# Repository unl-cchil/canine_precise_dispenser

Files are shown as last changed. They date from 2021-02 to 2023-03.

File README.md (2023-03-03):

# Raspberry Pi controlled precise treat dispenser
**This project provides the source for a precise canine treat dispenser designed for numerical discrimination tasks.**

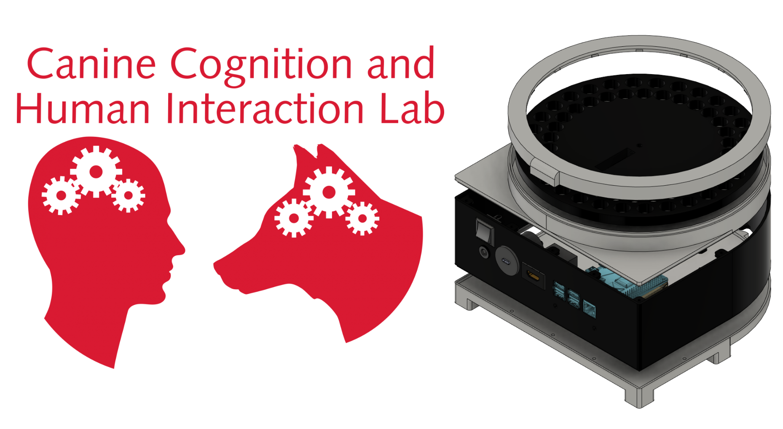
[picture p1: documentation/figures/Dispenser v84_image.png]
Precise Dispenser

### Overview
For detailed overview, review the [user guide](https://github.com/unl-cchil/canine_precise_dispenser/blob/main/documentation/user_guide/unl_cchil_precise_dispenser_guide.pdf) or the [Journal of Open Hardware paper](http://doi.org/10.5334/joh.41).  The basic operating principles of the dispenser can be seen in our [YouTube demo video](https://www.youtube.com/watch?v=fIKlNvzwXUY) or in [this embedded video](https://github.com/unl-cchil/canine_precise_dispenser/blob/main/hardware/dispenser/operation/show_dispenser_video.md).

By using the embedded Python library in the Raspberry Pi image, which is also included in this repository, the stepper motor can be controlled to position the treat holes over the pellet exhaust, leading to a dispensation.  By chaining these events together, a specified quantity of treats can be dispensed.  Additionally, the image is configured with a working build of PsychoPy (v3.2.4).

### Raspberry Pi Image
The SD card image for the Raspberry Pi has all dependencies installed and only needs to have its access point configured using pi-ap.  The image can be found [here](https://drive.google.com/file/d/1Q6JxdohXtvS-_8pmgR74lJ5-K5ArOl2h/view?usp=sharing).  Use an SD card flasher to write this image to a bootable media, such as balenaEtcher, Win32DiskImager, or other similar software.

### Interfacing Example
```
from precise_dispenser_driver import PreciseDispenser

dispenser = PreciseDispenser()
try:
	dispenser.dispense_treats(10)
	print(“Successfully dispensed ten treats.”)
except ValueError as e:
	print(e)
dispenser.close()
```

### License
The hardware is available under a [CERN-OHL-S-2.0 license](https://spdx.org/licenses/CERN-OHL-S-2.0.html), found [here](https://github.com/unl-cchil/canine_precise_dispenser/blob/main/HWLICENSE.md).

The software is available under an [MIT license](https://opensource.org/licenses/MIT), found [here](https://github.com/unl-cchil/canine_precise_dispenser/blob/main/SWLICENSE.md).

The documentation is available under a [Creative Commons Attribution-ShareAlike 4.0 International Public License (CC BY-SA 4.0)](https://creativecommons.org/licenses/by-sa/4.0/), found [here](https://github.com/unl-cchil/canine_precise_dispenser/blob/main/LICENSE.md).

### Project Mentions
[Hackaday](https://hackaday.com/2022/02/06/open-hardware-dog-treat-dispenser-is-a-stepping-stone-for-behavioral-research/), [UNL Pocket Science](https://news.unl.edu/newsrooms/today/article/lab-s-best-friend-3d-printed-dog-treat-dispenser-outperforms-predecessors/)

### Contact
This project was conducted by the [Canine Cognition and Human Interaction Lab](https://dogcog.unl.edu). For questions, please contact the developer Walker Arce (warce@unomaha.edu) or the principal investigator Jeffrey R. Stevens (jeffrey.r.stevens@gmail.com).

### Citation
Arce, W., and Stevens, J. R. (2022). A precise dispenser design for canine cognition research. _Journal of Open Hardware_, 6(1), 2. http://doi.org/10.5334/joh.41

### Funding
This research was supported by a National Science Foundation grant (SES-1658837) and a University of Nebraska-Lincoln Research Council Grant-in-Aid to JRS.

### Dataset Metadata
The following table is necessary for this dataset to be indexed by search
engines such as <a href="https://g.co/datasetsearch">Google Dataset Search</a>.
<div itemscope itemtype="http://schema.org/Dataset">
<table>
<tr>
<th>property</th>
<th>value</th>
</tr>
<tr>
<td>name</td>
<td><code itemprop="name">A precise dispenser design for canine cognition research reliability testing dataset</code></td>
</tr>
<tr>
<td>description</td>
<td><code itemprop="description">The dataset from the paper [A precise dispenser design for canine cognition research](http://doi.org/10.5334/joh.41). We tested five treat dispensers 100 times each with 10 tests of increasing dispensing targets from 1 to 10 treats. Each row of the data file gives the expected and actual number of treats dispensed for a single trial.</code></td>
</tr>
</tr>
<tr>
<td>url</td>
<td><code itemprop="url">https://github.com/unl-cchil/canine_precise_dispenser</code></td>
</tr>
<tr>
<td>sameAs</td>
<td><code itemprop="sameAs">https://github.com/unl-cchil/canine_precise_dispenser</code></td>
</tr>
<tr>
<td>citation</td>
<td><code itemprop="citation">TBA</code></td>
</tr>
<tr>
<td>hw license</td>
<td>
<div itemscope itemtype="http://schema.org/CreativeWork" itemprop="license">
<table>
<tr>
<th>property</th>
<th>value</th>
</tr>
<tr>
<td>name</td>
<td><code itemprop="name">CERN-OHL-S-2.0</code></td>
</tr>
<tr>
<td>url</td>
<td><code itemprop="url">https://spdx.org/licenses/CERN-OHL-S-2.0.html</code></td>
</tr>
</table>
</div>
</td>
</tr>
<tr>
<td>sw license</td>
<td>
<div itemscope itemtype="http://schema.org/CreativeWork" itemprop="license">
<table>
<tr>
<th>property</th>
<th>value</th>
</tr>
<tr>
<td>name</td>
<td><code itemprop="name">MIT</code></td>
</tr>
<tr>
<td>url</td>
<td><code itemprop="url">https://opensource.org/licenses/MIT</code></td>
</tr>
</table>
</div>
</td>
</tr>
<tr>
<td>docs license</td>
<td>
<div itemscope itemtype="http://schema.org/CreativeWork" itemprop="license">
<table>
<tr>
<th>property</th>
<th>value</th>
</tr>
<tr>
<td>name</td>
<td><code itemprop="name">CC BY-SA 4.0</code></td>
</tr>
<tr>
<td>url</td>
<td><code itemprop="url">https://creativecommons.org/licenses/by-sa/4.0/</code></td>
</tr>
</table>
</div>
</td>
</tr>
</table>
</div>

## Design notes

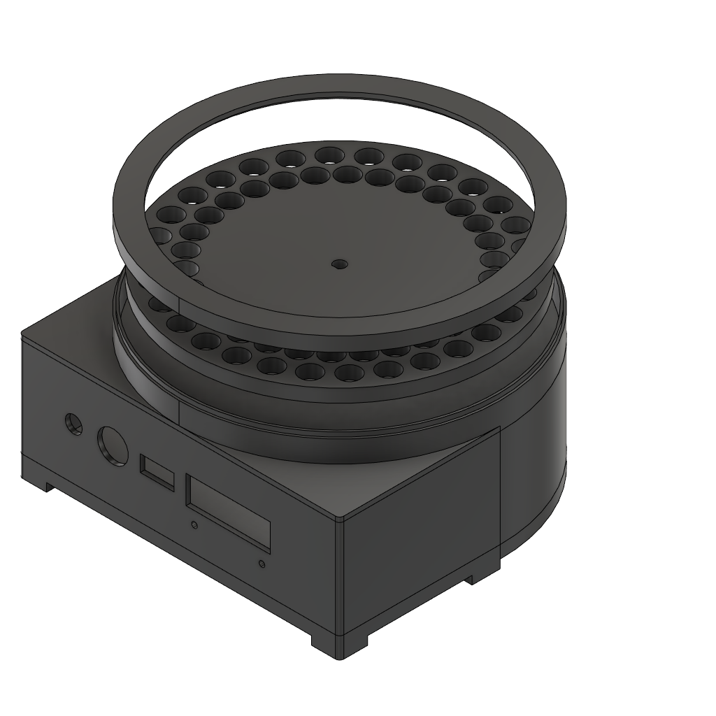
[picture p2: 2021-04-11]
hardware/dispenser/renders/Dispenser v55.png

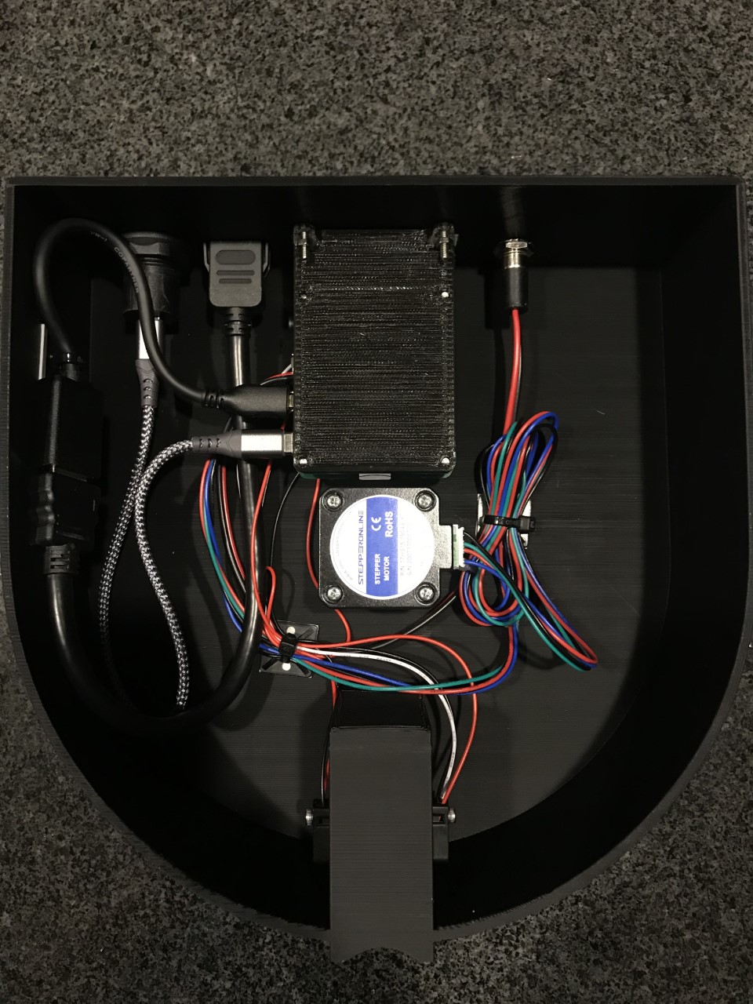
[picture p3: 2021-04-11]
hardware/dispenser/pictures/finished_prototype.jpg

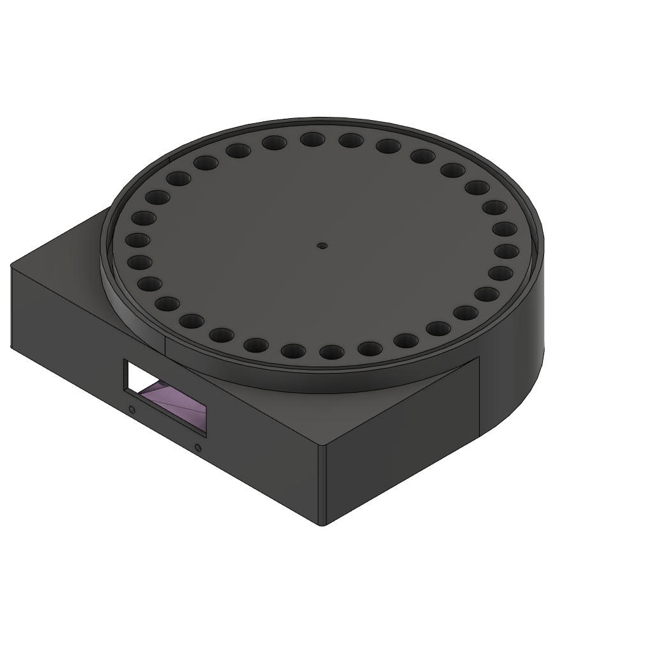
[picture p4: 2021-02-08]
hardware/dispenser/renders/Dispenser v12.png

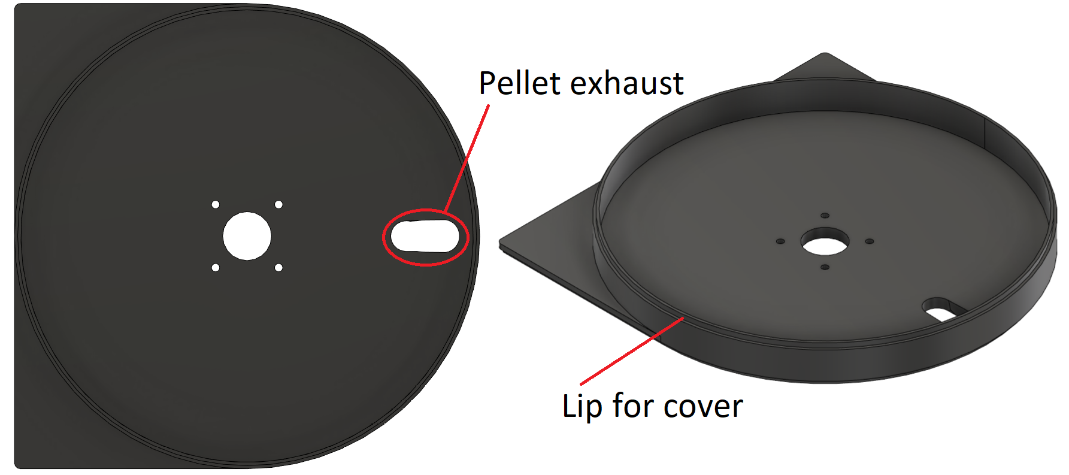
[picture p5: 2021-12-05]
documentation/paper/figures/figure4.png

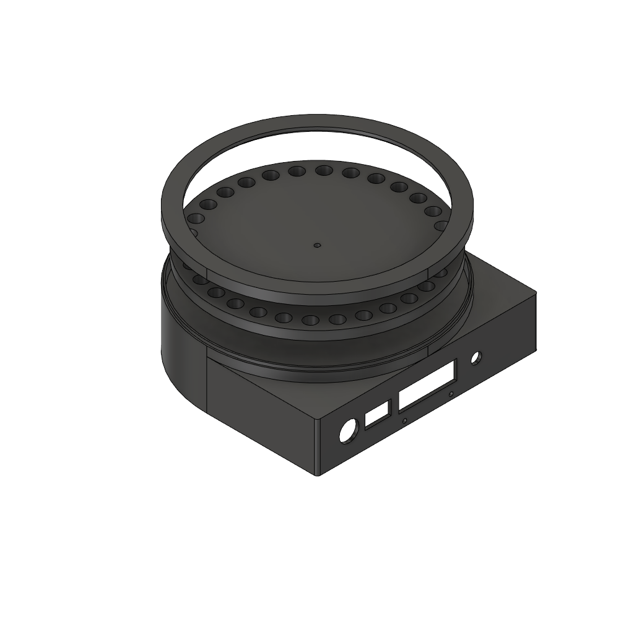
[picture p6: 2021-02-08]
hardware/dispenser/renders/Dispenser v17.png

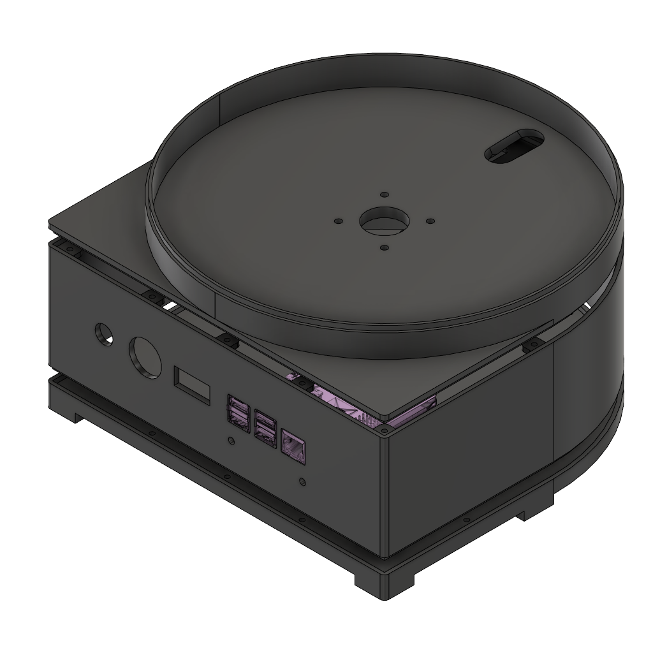
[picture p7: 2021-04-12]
hardware/dispenser/renders/Dispenser v61 - No wheel or cover.png

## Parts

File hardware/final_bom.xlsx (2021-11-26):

Bill of Materials - Precise Dispenser
Part | Quantity | Cost | Link |  | Use
1 kg natural filament | 1 | $22.99 | Filament (https://www.amazon.com/OVERTURE-Filament-Consumables-Dimensional-Accuracy/dp/B07PGY2JP1) | Amazon | Used to print the dispenser
Raspberry Pi 4 | 1 | $75.00 | Raspberry Pi (https://www.sparkfun.com/products/15447) | SparkFun | Controls the dispenser
HDMI Panel Mount | 1 | $7.95 | HDMI (https://www.digikey.com/en/products/detail/4054/1528-2888-ND/9997693?itemSeq=352933947) | DigiKey | Breaks out HDMI connection on Pi to connector panel
USB C Panel Mount | 1 | $7.50 | USB C (https://www.digikey.com/en/products/detail/4261/1528-4261-ND/10287031?itemSeq=352933946) | DigiKey | Breaks out 5V USB power on Pi to connector panel
Barrel Jack Panel Mount | 1 | $5.17 | Barrel Jack (https://www.digikey.com/en/products/detail/10-02879/839-1449-ND/8635386?itemSeq=352933944) | DigiKey | Breaks out 12V power on Pi HAT to connector panel
HDMI to Micro HDMI | 1 | $8.69 | Micro HDMI (https://www.amazon.com/GANA-Adapter-Female-Action-Supported/dp/B07K21HSQX) | Amazon | Converts the HDMI panel connector to Micro HDMI on Pi
Stepper Motor Power Supply | 1 | $11.61 | 12V Power (https://www.digikey.com/en/products/detail/tensility-international-corp/16-00143/10324430) | DigiKey | 12V power supply for stepper motor
Stepper Motor | 1 | $8.99 | Motor (https://www.amazon.com/gp/product/B087BWKJZP/ref=ox_sc_act_title_1?smid=A2TMK1RHV496EY&th=1) | Amazon | Motor to drive the treat jogger
Raspberry Pi Power Supply | 1 | $8.00 | Pi Power (https://www.sparkfun.com/products/15448) | SparkFun | 5V power supply for Raspberry Pi
Plastic Cover | 1 | $11.49 | 8 in Cover (https://www.amazon.com/gp/product/B083HNZWK6/ref=ox_sc_act_title_2?smid=A2PYYAAPQIARBH&psc=1) | Amazon | Acrylic plate to cover the treats from the environment
IR Break Beam | 1 | $6.50 | 5mm IR (https://www.adafruit.com/product/2167) | Adafruit | External sensors to detect a treat falling from jogger
Cable Ties | 1 | $9.69 | Zip Ties and Mounts (https://www.amazon.com/gp/product/B08F77YVYB/ref=ppx_yo_dt_b_asin_title_o00_s00?ie=UTF8&psc=1) | Amazon | Used to hold down wires within the dispenser
Micro SD Card | 1 | $6.49 | SD Card Pack (https://www.amazon.com/Micro-Center-Class-Memory-Adapter/dp/B07K835MNR) | Amazon | Used to hold data and OS on Raspberry Pi
USB C Cable | 1 | $6.99 | USB C Cables (https://www.amazon.com/JXMOX-Charger-Charging-Compatible-2018-Grey/dp/B07TVMBZ75) | Amazon | Connects the panel USB C to Raspberry Pi
Power Switch | 1 | $1.34 | Switch (https://www.digikey.com/en/products/detail/e-switch/RA41G31900/8540802) | DigiKey | Double pull double throw switch for both 5V and 12V power
A4988 Stepper Motor | 1 | $4.69 | Motor Driver (https://www.amazon.com/HiLetgo-Stepstick-Stepper-Printer-Compatible/dp/B00LOF1CA2) | Amazon | Placed on Pi HAT into the female headers
2 Pin Screw Terminal | 2 | $2.20 | 2x 3.5mm Terminal (https://www.digikey.com/en/products/detail/w%C3%BCrth-elektronik/691214110002S/11477397) | DigiKey | Soldered to Pi HAT
3 Pin Screw Terminal | 1 | $1.35 | 3x 3.5mm Terminal (https://www.digikey.com/en/products/detail/w%C3%BCrth-elektronik/691214110003S/11477432) | DigiKey | Soldered to Pi HAT
Capacitor | 1 | $0.13 | 10u TH Cap (https://www.digikey.com/en/products/detail/w%C3%BCrth-elektronik/860240572001/5729254) | DigiKey | Soldered to Pi HAT
Resistor | 1 | $0.10 | 10k TH Res (https://www.digikey.com/en/products/detail/stackpole-electronics-inc/CF14JT10K0/1741265) | DigiKey | Soldered to Pi HAT
40 Pin Header | 1 | $2.29 | Pi Header (https://www.digikey.com/en/products/detail/sullins-connector-solutions/PPTC202LFBN-RC/807240) | DigiKey | Soldered to Pi HAT
Stepper Motor Header | 1 | $0.20 | 4 Pin Right Angle (https://www.digikey.com/en/products/detail/harwin-inc/M20-9750446/3727931) | DigiKey | Soldered to Pi HAT
A4988 Female Pins | 1 | $0.65 | 2x Female Headers (https://www.digikey.com/en/products/detail/sullins-connector-solutions/PPTC081LFBN-RC/810147) | DigiKey | Soldered to Pi HAT

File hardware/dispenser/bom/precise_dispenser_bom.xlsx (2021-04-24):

Bill of Materials - Precise Dispenser
Part | Quantity | Cost | Link
1 kg black filament | 1 | $19.99 | Filament (https://www.amazon.com/OVERTURE-Filament-Consumables-Dimensional-Accuracy/dp/B07PGY2JP1)
Raspberry Pi 4 | 1 | $55.00 | Raspberry Pi (https://www.sparkfun.com/products/15447)
HDMI Panel Mount | 1 | $7.95 | HDMI (https://www.digikey.com/en/products/detail/4054/1528-2888-ND/9997693?itemSeq=352933947)
USB C Panel Mount | 1 | $7.50 | USB C (https://www.digikey.com/en/products/detail/4261/1528-4261-ND/10287031?itemSeq=352933946)
Barrel Jack Panel Mount | 1 | $5.17 | Barrel Jack (https://www.digikey.com/en/products/detail/10-02879/839-1449-ND/8635386?itemSeq=352933944)
HDMI to Micro HDMI | 1 | $8.69 | Micro HDMI (https://www.amazon.com/GANA-Adapter-Female-Action-Supported/dp/B07K21HSQX)
Stepper Motor Power Supply | 1 | $11.61 | 12V Power (https://www.digikey.com/en/products/detail/tensility-international-corp/16-00143/10324430)
Stepper Motor | 1 | $8.99 | Motor (https://www.amazon.com/gp/product/B087BWKJZP/ref=ox_sc_act_title_1?smid=A2TMK1RHV496EY&th=1)
Raspberry Pi Power Supply | 1 | $8.00 | Pi Power (https://www.sparkfun.com/products/15448)
Plastic Cover | 1 | $9.95 | 8 in Cover (https://www.amazon.com/gp/product/B083HNZWK6/ref=ox_sc_act_title_2?smid=A2PYYAAPQIARBH&psc=1)
IR Break Beam | 1 | $1.95 | 3mm IR (https://www.adafruit.com/product/2167)
Cable Ties | 1 | $9.69 | Zip Ties and Mounts (https://www.amazon.com/gp/product/B08F77YVYB/ref=ppx_yo_dt_b_asin_title_o00_s00?ie=UTF8&psc=1)
Micro SD Card | 1 | $6.49 | SD Card Pack (https://www.amazon.com/Micro-Center-Class-Memory-Adapter/dp/B07K835MNR)
USB C Cable | 1 | $6.99 | USB C Cables (https://www.amazon.com/JXMOX-Charger-Charging-Compatible-2018-Grey/dp/B07TVMBZ75)

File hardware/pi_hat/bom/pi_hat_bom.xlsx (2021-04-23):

Bill of Materials - Precise Dispenser Pi HAT
Part | Quantity | Cost | Link
A4988 Stepper Motor | 1 | $4.69 | Motor Driver (https://www.amazon.com/HiLetgo-Stepstick-Stepper-Printer-Compatible/dp/B00LOF1CA2)
2 Pin Screw Terminal | 2 | $2.20 | 2x 3.5mm Terminal (https://www.digikey.com/en/products/detail/w%C3%BCrth-elektronik/691214110002S/11477397)
3 Pin Screw Terminal | 1 | $1.35 | 3x 3.5mm Terminal (https://www.digikey.com/en/products/detail/w%C3%BCrth-elektronik/691214110003S/11477432)
Capacitor | 1 | $0.13 | 10u TH Cap (https://www.digikey.com/en/products/detail/w%C3%BCrth-elektronik/860240572001/5729254)
Resistor | 1 | $0.10 | 10k TH Res (https://www.digikey.com/en/products/detail/stackpole-electronics-inc/CF14JT10K0/1741265)
40 Pin Header | 1 | $2.29 | Pi Header (https://www.digikey.com/en/products/detail/sullins-connector-solutions/PPTC202LFBN-RC/807240)
Stepper Motor Header | 1 | $0.20 | 4 Pin Right Angle (https://www.digikey.com/en/products/detail/harwin-inc/M20-9750446/3727931)
A4988 Female Pins | 2 | $1.30 | 2x Female Headers (https://www.digikey.com/en/products/detail/sullins-connector-solutions/PPTC081LFBN-RC/810147)

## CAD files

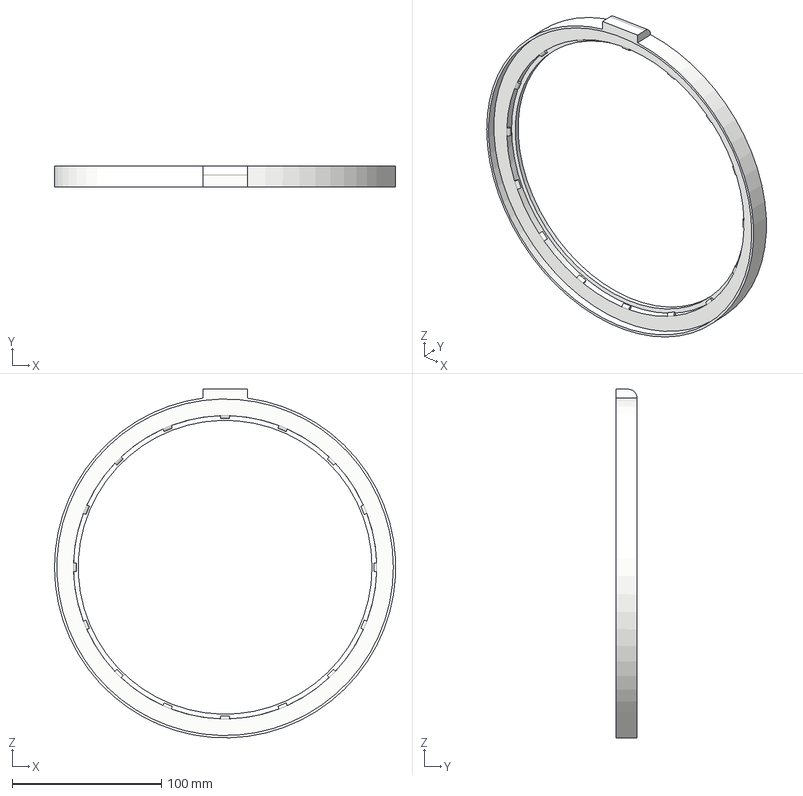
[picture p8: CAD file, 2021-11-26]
hardware/dispenser/step/dispenser_cover.step
228.4 x 14.2 x 233.6 mm

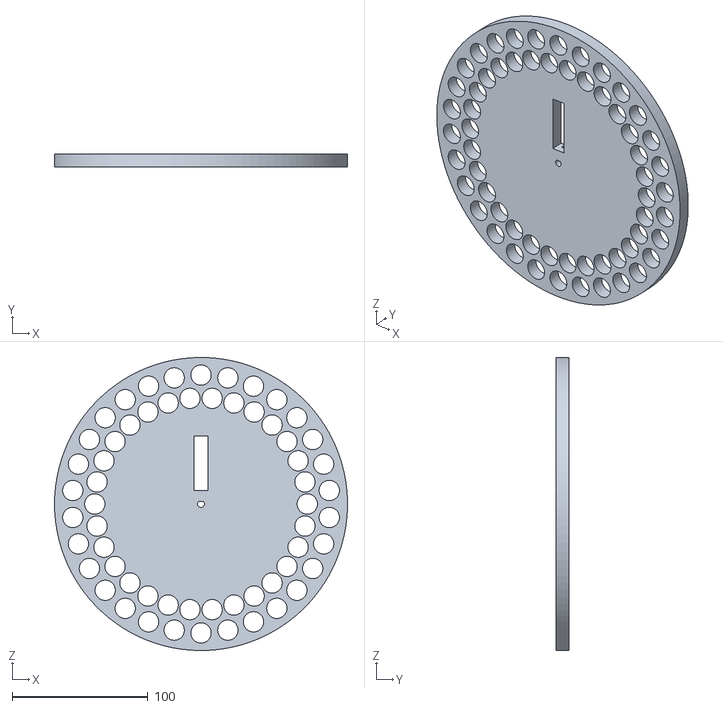
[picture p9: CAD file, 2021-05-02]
hardware/dispenser/stls/dispenser_wheel.stl
215.9 x 9.35 x 215.9

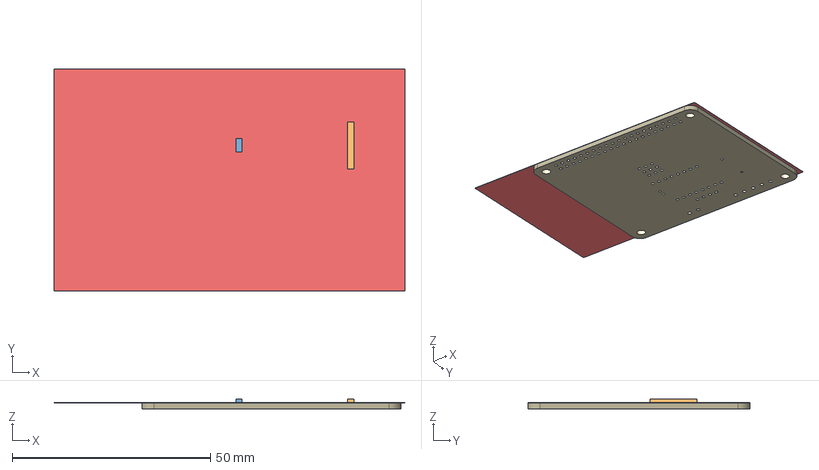
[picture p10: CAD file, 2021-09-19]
hardware/pi_hat/renders/DispenserV2.0.step
88.5 x 56.1 x 2.57 mm
Board
E2-5
SCREWTERMINAL-3.5MM-2 x 2
455-1750-1-ND x 3
A4988
1X04
0207/10
SCREWTERMINAL-3.5MM-3
RASPBERRY_PI_3_MODEL_B+

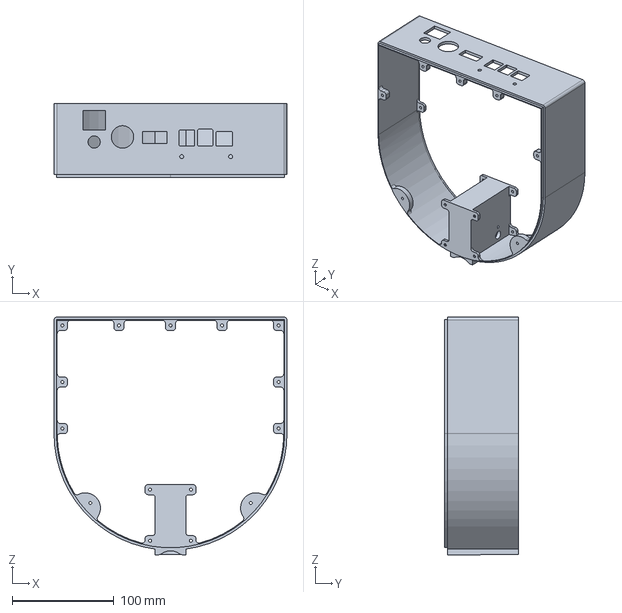
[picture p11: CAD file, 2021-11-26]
hardware/dispenser/step/dispenser_walls.step
228.6 x 72.9 x 233.3 mm

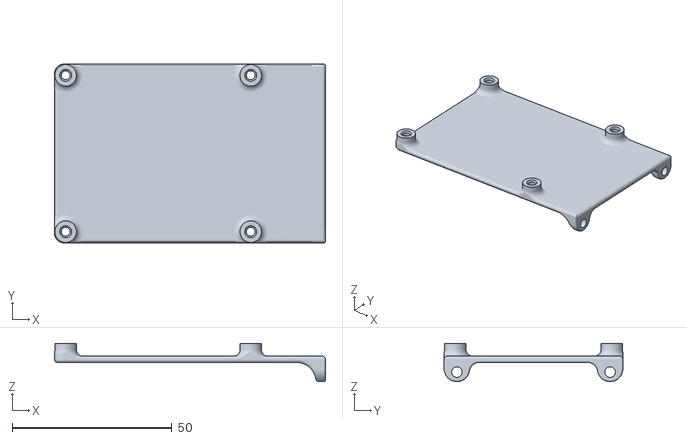
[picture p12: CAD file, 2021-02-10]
hardware/dispenser/stls/dispenser_pi_mount.stl
84.9 x 56.0 x 12.0

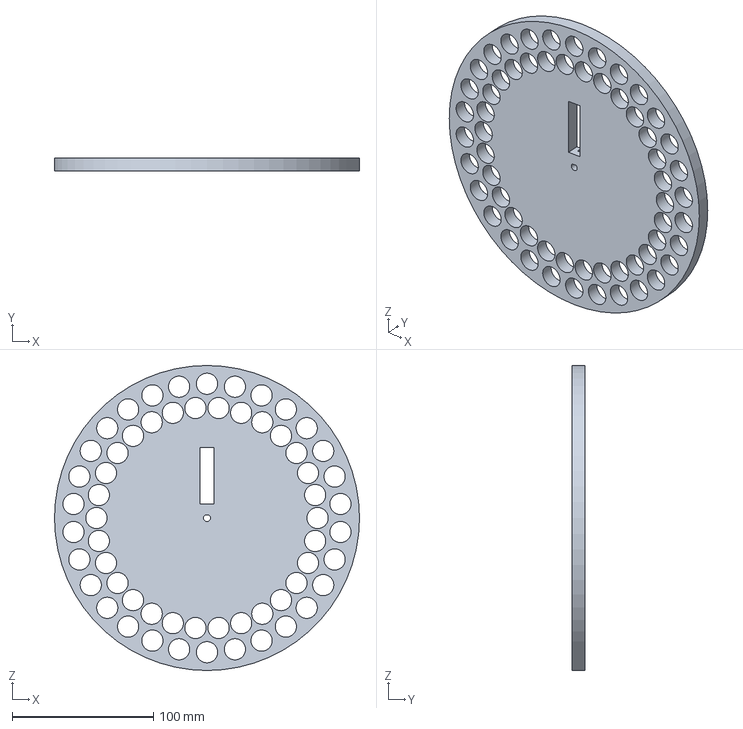
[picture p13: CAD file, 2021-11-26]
hardware/dispenser/step/treat_jogger.step
215.9 x 9.35 x 215.9 mm

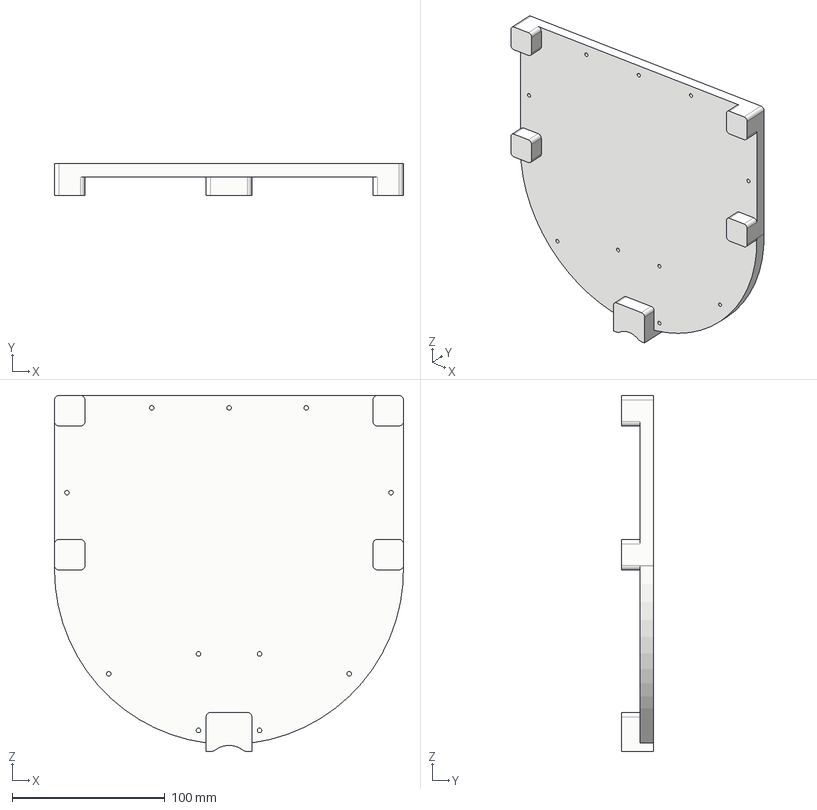
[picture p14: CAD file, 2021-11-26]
hardware/dispenser/step/dispenser_bottom.step
228.6 x 21.0 x 233.3 mm

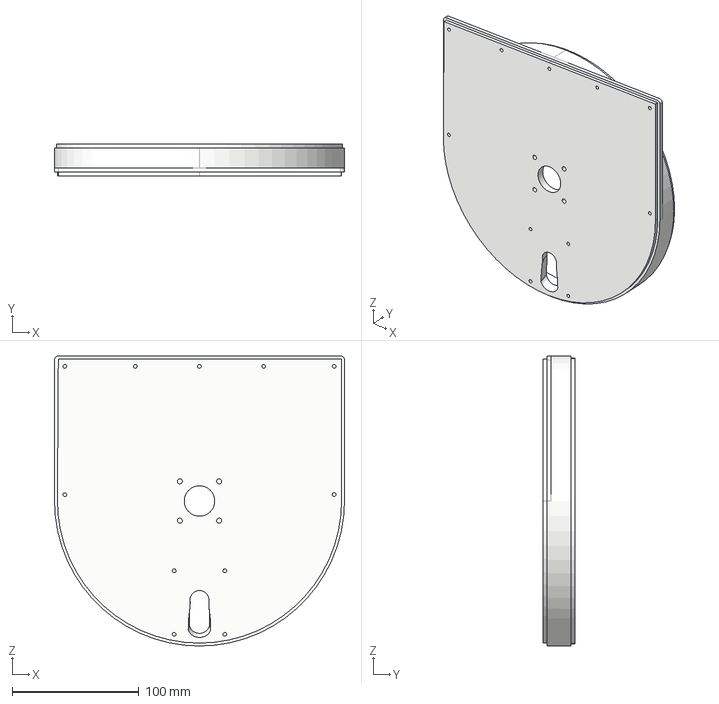
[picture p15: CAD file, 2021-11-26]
hardware/dispenser/step/dispenser_top.step
228.6 x 25.1 x 228.6 mm

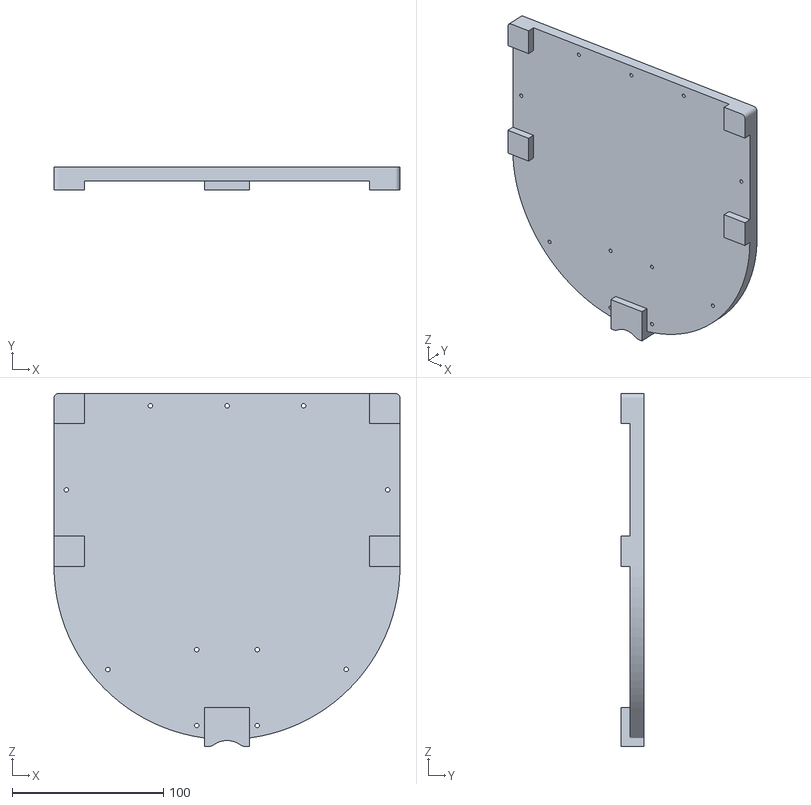
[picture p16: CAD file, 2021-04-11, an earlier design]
hardware/dispenser/stls/Old/dispenser_bottom.stl
228.6 x 15.0 x 233.3

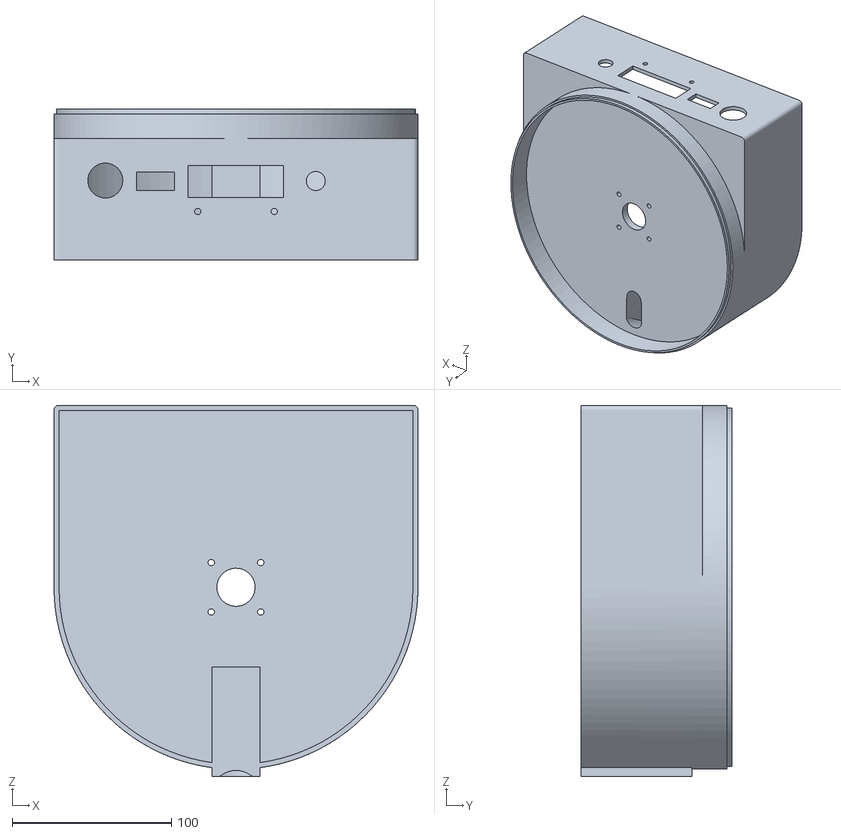
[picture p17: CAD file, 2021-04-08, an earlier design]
hardware/dispenser/stls/Old/dispenser_body.stl
228.6 x 94.9 x 233.3

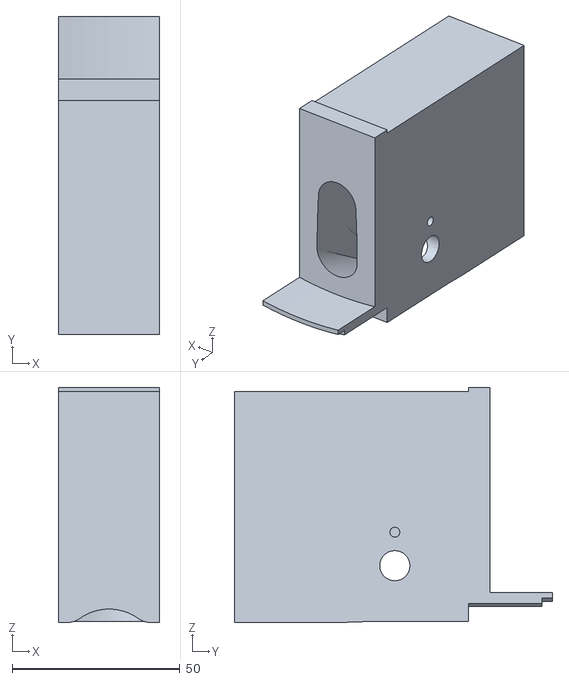
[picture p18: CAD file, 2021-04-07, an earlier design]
hardware/dispenser/stls/Old/dispenser_pellet_exhaust.stl
30.0 x 94.9 x 70.1

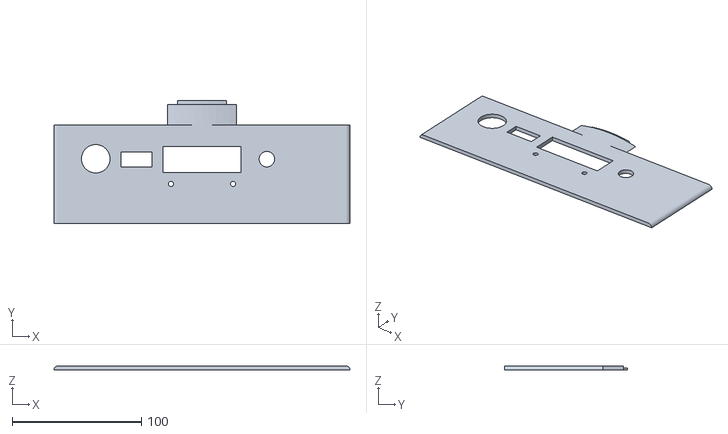
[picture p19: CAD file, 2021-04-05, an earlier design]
hardware/dispenser/stls/Old/dispenser_interface.stl
228.6 x 94.9 x 3.18

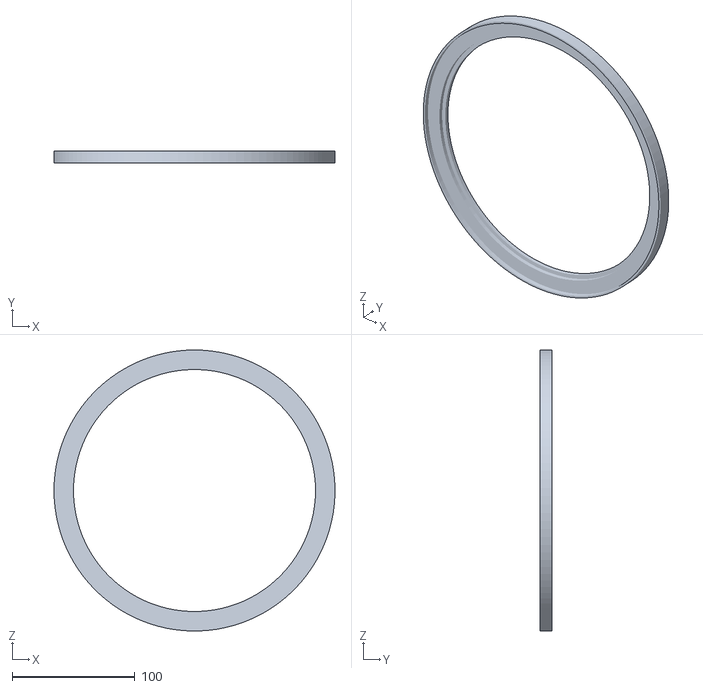
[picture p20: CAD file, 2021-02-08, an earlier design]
hardware/dispenser/stls/Old/dispenser_cover.stl
228.6 x 10.2 x 228.6

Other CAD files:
hardware/dispenser/step/pi_mount.step
hardware/dispenser/stls/Old/dispenser_top.stl
hardware/dispenser/stls/Old/dispenser_walls.stl
hardware/dispenser/stls/Old/dispenser_wheel.stl
hardware/dispenser/source/Dispenser v18.f3d
hardware/dispenser/source/Dispenser v22.f3d
hardware/dispenser/source/Dispenser v30.f3d
hardware/dispenser/source/Dispenser v31.f3d
hardware/dispenser/source/Dispenser v35.f3d
hardware/dispenser/source/Dispenser v39.f3d
hardware/dispenser/source/Dispenser v55.f3d
hardware/dispenser/stls/dispenser_bottom.stl
hardware/dispenser/stls/dispenser_cover.stl
hardware/dispenser/stls/dispenser_top.stl
hardware/dispenser/stls/dispenser_walls.stl

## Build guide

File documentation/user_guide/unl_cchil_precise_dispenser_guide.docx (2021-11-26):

University of Nebraska – Lincoln

Department of Psychology

Canine Cognition and Human Interaction Laboratory

Dr. Jeffrey R. Stevens

Precise Dispenser for Canine Numerical Discrimination Tasks

20 September 2021

V0.4

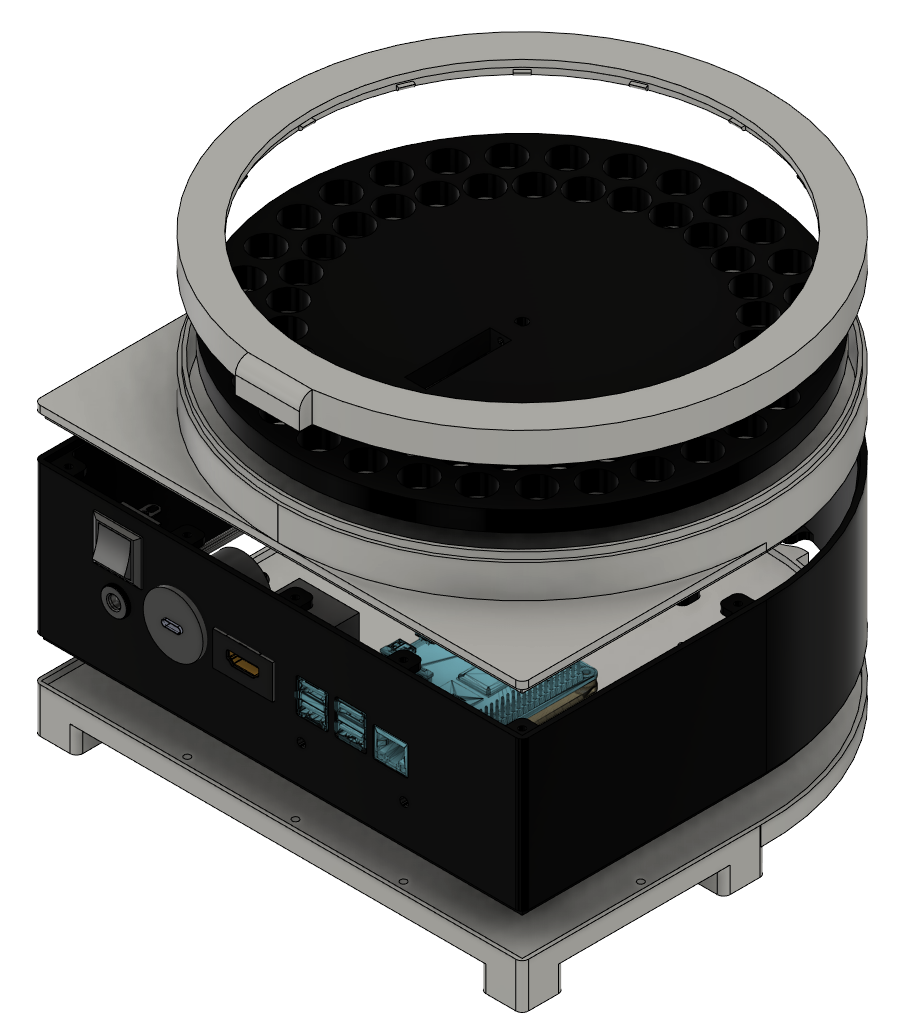
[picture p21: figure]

Figure 1 – Dispenser v84 Render

Overview

The performance of canine numerical discrimination tasks can be hindered by a lack of appropriate instrumentation. Using manual, researcher-controlled instrumentation can introduce a reaction time variable that could impose undue variability in the task results. Therefore, the creation of devices that can automatically dispense precise numbers of treats at the introduction of a predefined stimulus can be justified.

Dispenser Operation

The precise dispenser has a wheel on the top of it that holds up to 59 treats. The stepper motor shaft interfaces to the dispenser wheel through the center hole and by actuating the motor, the holes for the treat lines up with the treat exhaust and falls to the bowl below. When the treat goes through the exhaust it breaks an infrared break beam and the Raspberry Pi detects the treat dispensing.

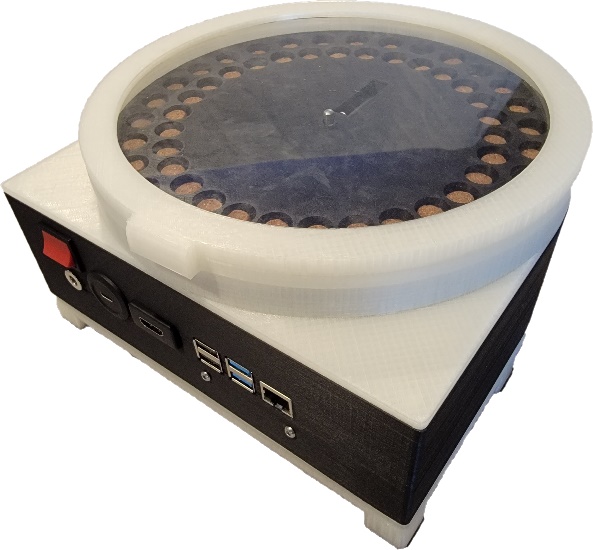
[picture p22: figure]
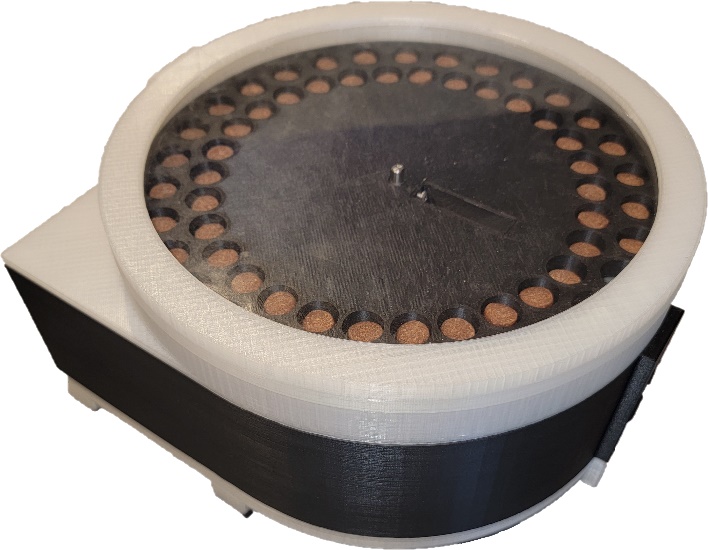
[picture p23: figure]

Figure 2 – Images of the assembled dispenser, fully loaded with treats

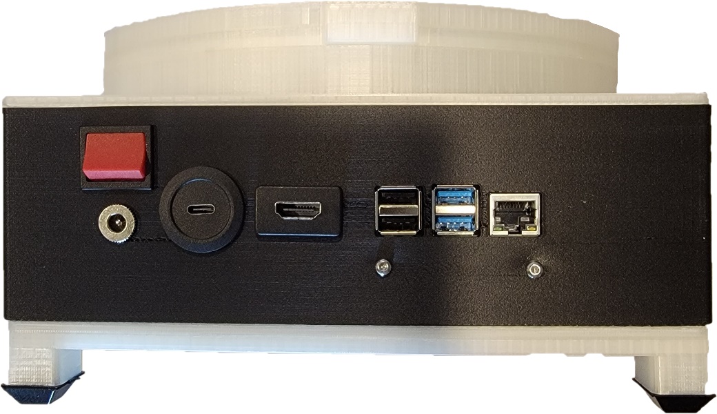
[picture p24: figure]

Figure 3 – Assembled dispenser connector backplane

Build Instructions

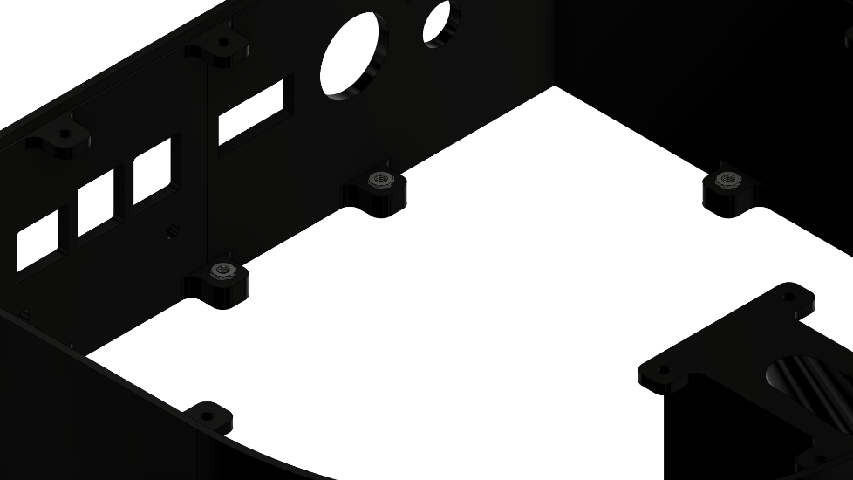
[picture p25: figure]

Observe the M3 hex nut capture slots on the dispenser walls. In each of these, super glue an M3 hex nut. Let it sit for 24 hours before continuing.

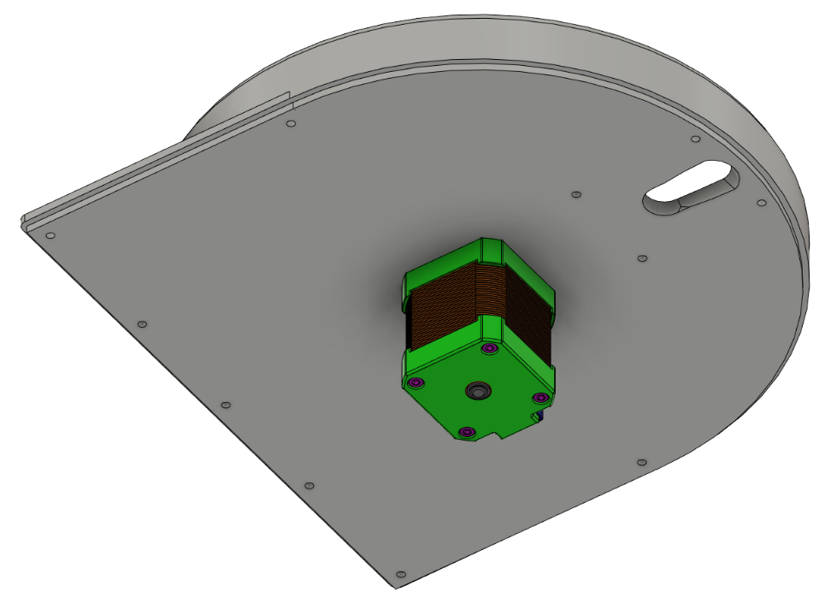
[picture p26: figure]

Mount the Nema 17 stepper motor using pan head M3 screws. Ensure the connector is point towards the right side, as shown.

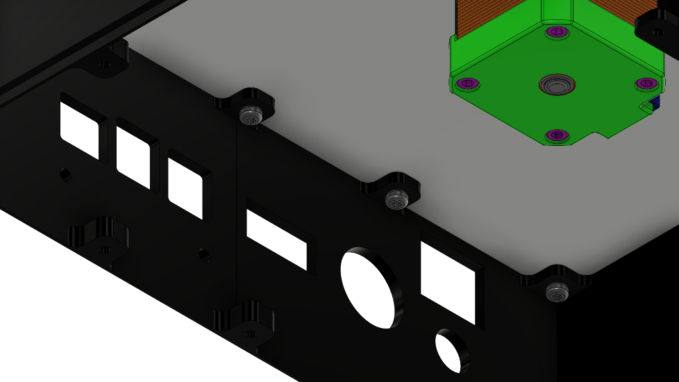
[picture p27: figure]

At this point, use 6mm M3 screws to mount the walls to the top of the dispenser. Mount the dispenser jogger by press fitting it onto the stepper motor shaft. Ensure the motor is supported during this, as it will break through the print when pressing the jogger down.

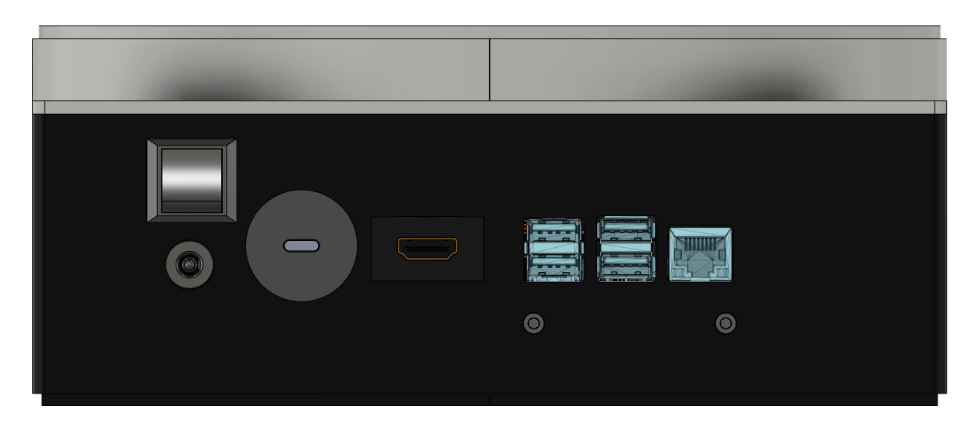
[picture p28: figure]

Now, mount the Raspberry Pi to the right angle mount using four M3 screws. Then, mount this into the walls using a 10mm M3 screw with hex nuts. Then mount the other panel mount connectors into the walls.

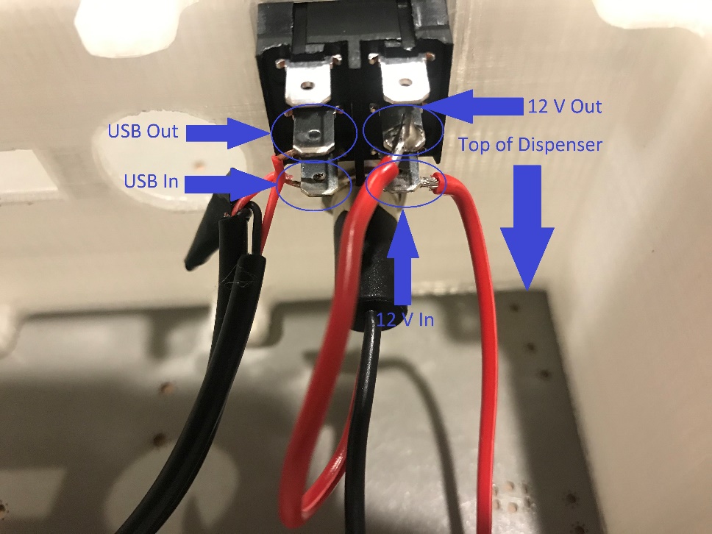
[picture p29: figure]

With the DPDT switch mounted, cut a USB C to USB C cord and solder the grounds back together. Cut the barrel jack panel mount connector’s red wire, with one fifth of it being close to the connector and the other four fifths being used to connect to the Pi HAT. Solder according to image.

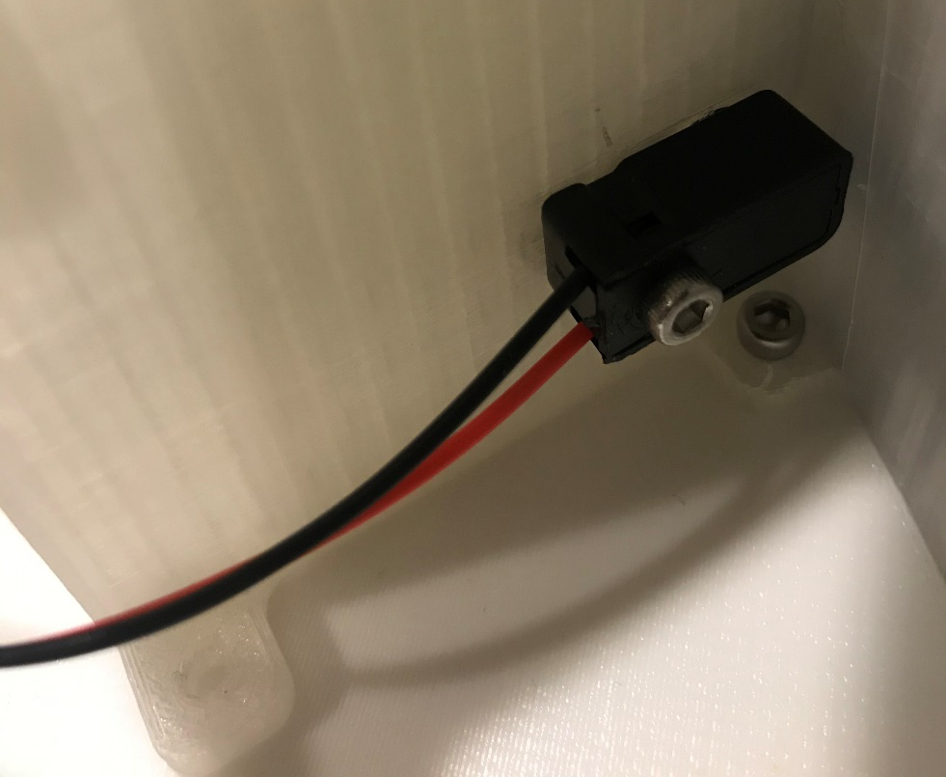
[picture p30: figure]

Mount the IR phototransistor elements to the side of the pellet exhaust using 9mm M3 screws.

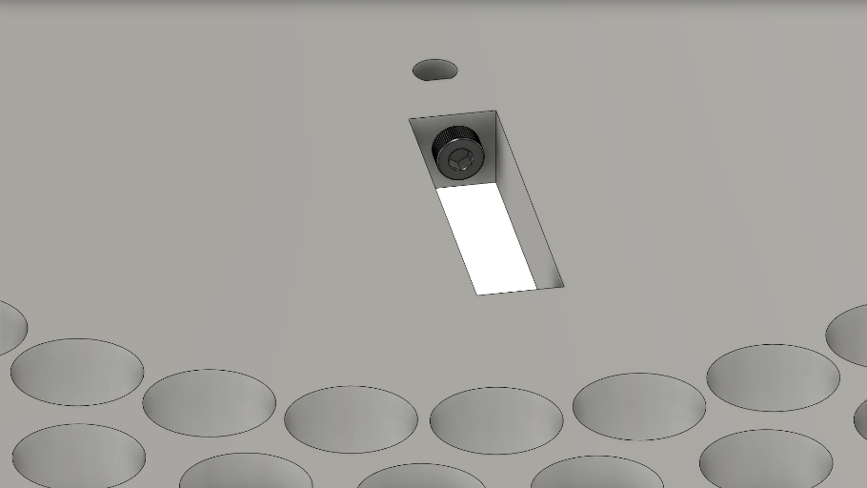
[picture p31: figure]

Place a 12mm M3 in the set screw hole of the treat jogger and screw it down to hold the jogger to the motor shaft.

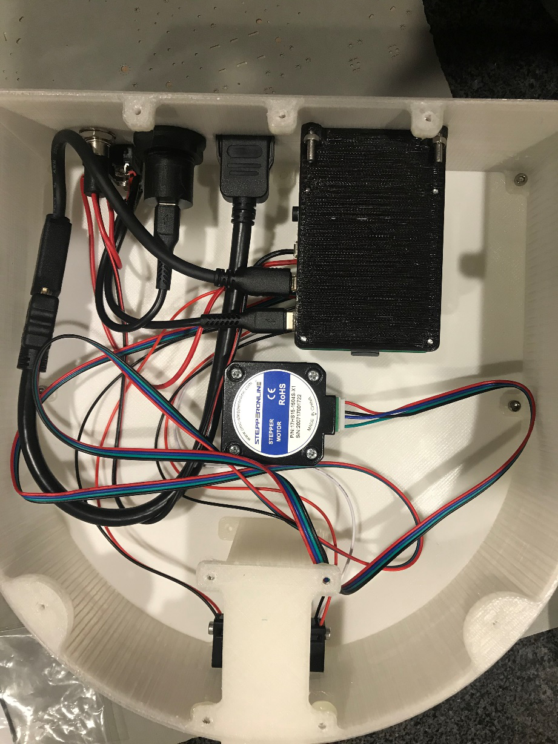
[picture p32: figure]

Wire up the remaining pieces as shown below. Secure the wires using the square zip tie mounts.

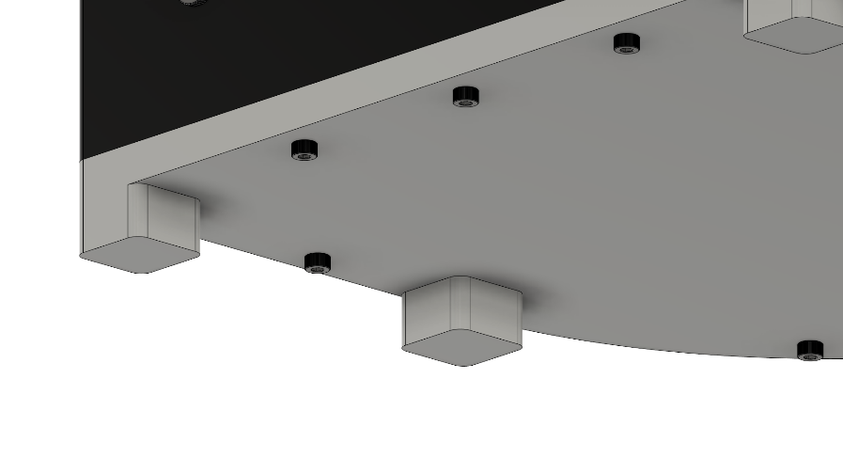
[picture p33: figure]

Screw on the bottom plate using 6mm M3 screws. It is recommended to use rubber anti slip pads on the legs of the dispenser. Place the acrylic disk into the cover and place the cover onto the dispenser.

Testing Operation

1. Place treats into all the holes of the treat jogger and manually rotate the wheel to ensure all treats fall out of the holes. If some stick, then make sure any strands are removed from the print.
2. The dispenser_test.py script can be used to ensure the break beam works and that treats are dispensed as expected.

Troubleshooting

1. If the dispenser under dispenses, ensure the treat jogger is mounted securely to the motor shaft. If the set screw strips the hole, use super glue to affix the wheel to the shaft.
2. If the dispenser over dispenses, ensure that the jogger is perfectly aligned over the pellet exhaust before use.

Python Class Definition

class PreciseDispenser

self.loaded_treats

The number of treats remaining the in the jogger

self.dispensing_timeout

The amount of time between IR break beam events before an exception is thrown

self.dispensing

A Boolean to track if the dispenser is currently dispensing

__init__(loaded_treats, timeout=1)

Initializer for the canine treat dispenser, configures control variables and Pi GPIO.

:param loaded_treats: The number of treats that are loaded into the dispenser for this session. Defaults to max, 59 treats.

:param timeout: The amount of time before the dispenser throw an error between dispensation events

dispense_treat()

Function to dispense a single treat. Should not be used, use dispense_treats for error handling.

:returns: True for successful dispensation of a single treat, False for a failure to dispense the treat.

dispense_treats(num_treats)

Dispenses the specified number of treats. If the requested number of treats is greater than the remaining treats, a ValueError is thrown. If the treat dispenser loop times out, a ValueError is thrown.

:param num_treats: A number between 1 and the remaining number of treats.

:returns: None. Throws ValueError when an error event is encountered. treat_dispensed(channel):

A callback function for when a treat is dispensed. This is detected on the falling edge of the IR break beam.

:param channel: The channel to identify the callback source.

:returns: None.

close()

Closes the dispenser object and cleans up the GPIO assignments.

:returns: None.

Interfacing Example

from precise_dispenser_driver import PreciseDispenser

dispenser = PreciseDispenser()

try:

dispenser.dispense_treats(10)

print(“Successfully dispensed ten treats.”)

except ValueError as e:

print(e)

dispenser.close()

Raspberry Pi 4 as an Experiment Platform

The experiments on canine operant conditioning are run using a Python package called PsychoPy. It essentially acts as a development environment for psychology experiments and provides a variety of utilities for user interface development, trigger conditions, experiment logging, and so on. Our aim is to integrate this directly into a Raspberry Pi 4, to allow the entire setup to become a mobile testing unit. To do this, we will have a few requirements:

1. Wireless Access Point
  a. The Raspberry Pi 4 should host its own WiFi access point (AP), which allows the experimenter to connect to the Pi and run experiments, download results, and interact with the main system.
2. Decoupled Interfaces
  a. The screen the experimenter will use, and the screen used by the canine will be separate and require no extra hardware to achieve. By connecting to the Pi using SSH (Secure Shell), the command line can be exposed to run the experiments. The canine screen can be connected to the HDMI0 of the Pi and the SSH session can be started in a separate area.
3. Simple Setup
  a. We want to make sure this is easy to setup and maintain. This means that we would want to use robust packages such as ‘pi-ap’ and SD card backups to easily restore the device and get new devices up and running easily.

There are two ways to setup a new Raspberry Pi to operate the canine dispenser:

1. Flash a new SD card with an image from the iso_images folder
  a. Using a Raspberry Pi with a fresh installation of Raspbian Buster, there are built-in tools to achieve this (https://www.raspberrypi.org/documentation/linux/filesystem/backup.md). “The SD Card Copier application, which can be found on the Accessories menu of the Raspberry Pi Desktop, will copy Raspbian from one card to another. To use it, you will need a USB SD card writer. To back up your existing Raspbian installation, put a blank SD card in your USB card writer and plug it into your Pi, and then launch SD Card Copier. In the ‘Copy From Device’ box, select the internal SD Card. This could have a number of different names and may have something like (/dev/mmcblk0) in its entry, but will usually be the first item in the list. Then select the USB card writer in the ‘Copy To Device’ box (where it will probably be the only device listed). Press ‘Start’. The copy, depending on the size of the SD card, can take ten or fifteen minutes, and when complete you should have a clone of your current installation on the new SD card. You can test it by putting the newly-copied card into the Pi’s SD card slot and booting it; it should boot and look exactly the same as your original installation, with all your data and applications intact.”
2. Follow the proceeding instructions to setup the Raspberry Pi manually.
  a. Flash a new copy of Rasbian Buster onto a micro SD card and place an empty file named “ssh” onto the boot partition. There is no file extension.
  b. Connect the Raspberry Pi to your local network using an Ethernet cable and power up the Pi. You can connect a monitor, keyboard, and mouse and use ifconfig to find the IP address of the Pi.
  c. Using this IP address, go to PuTTY and type in this IP address and connect to the Pi. The default password for “pi” is “raspberry”.
  d. Once in, the pi-ap software (https://github.com/f1linux/pi-ap) can be installed to create the access point. Note, the dog_operant repository does contain a copy of this, but the main repository will contain the most recent version.
  e. The dog_operant (https://github.com/adaptive-decision-making-lab/dog_operant) repository can be cloned using the git clone command.
  f. Run the command sudo apt-get update
  g. You will need to upgrade pip using python3 -m pip install --upgrade pip which will allow it to index some of the following packages.
  h. Run the command python3 -m pip install psychopy==3.2.4 which will install all the needed packages. Using the older version of PsychoPy will prevent a ‘Segmentation fault’ caused when rendering a new Window.
  i. You may have errors from installing PyQt5, to remedy this, try the following: sudo apt-get update

sudo apt-get install qt5-default pyqt5-dev pyqt5-dev-tools

  j. You may have errors importing Pandas due to an Import Error from NumPy, this can be fixed by doing: sudo apt-get install libatlas-base-dev
  k. You may get an error saying that there is no package called ‘wx’, in which case you need to run the command python3 -m pip install wxPython
  l. Step k may also error out, so issue the following command and then perform step k again: sudo apt-get install dpkg-dev build-essential libjpeg-dev libtiff-dev libsdl1.2-dev libgstreamer-plugins-base0.10-dev libnotify-dev freeglut3 freeglut3-dev libwebkitgtk-dev libghc-gtk3-dev libwxgtk3.0-gtk3-dev
  m. To install the audio tools, issue the following commands: sudo apt-get install portaudio19-dev

python3 -m pip install pysine

  n. To install the serial tools, issue the following command: python3 -m pip install pyserial
  o. If you want to run experiments, you will need to connect a screen to the Pi on HDMI0. An issue may present itself where no screen is presented when connected, which is caused by an incorrect /boot/config.txt file. To fix this do the following:
    i. sudo nano /boot/config.txt
    ii. Add the following to the file or uncomment from the file,
      1. hdmi_force_hotplug=1
      2. hdmi_drive=2
    iii. If this does not fix the issue, add,
      1. hdmi_safe=1
  p. To run an experiment, use the following command export DISPLAY=:0 ; python3 dog_operant/system_test.py Note, this works from the command line, so run this when you are connected to an SSH session and with a screen connected to HDMI0 of the Pi and the experiment will display over HDMI0. Setting the DISPLAY variable to 0 will default it to the local display.
3. To transfer the results of the experiments, copy the contents of the data directory from the dog_operant directory. Use the following command structure:  scp -r user@ssh.example.com:/path/to/remote/source /path/to/local/destination

Raspberry Pi Interfacing and Passwords

The dispenser, when turned on, will create a WiFi access point called, “cchil-precise-stevens-x”, with “x” being the number, i.e. “1”. By connecting to this, the Raspberry Pi can be accessed through SSH using a program called PuTTY (https://www.chiark.greenend.org.uk/~sgtatham/putty/latest.html).

Local Address | Password
pi@192.168.0.1 | raspberry
pi@cchil-precise-stevens-1 | raspberry

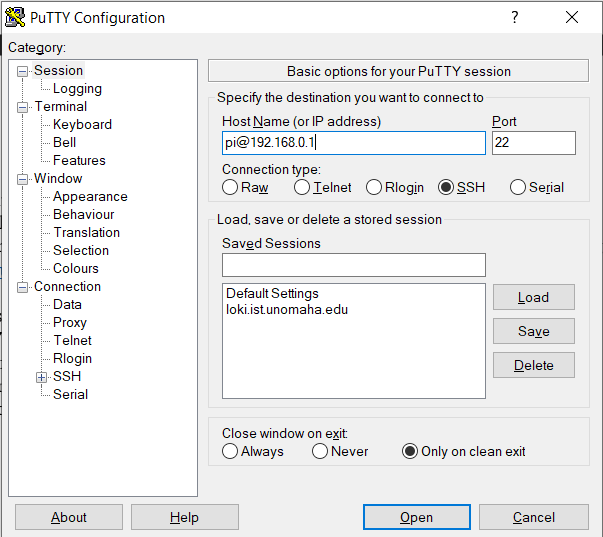
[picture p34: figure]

Figure 4 – PuTTY Terminal Configuration Window

Reliability Testing

We performed ten trials of increasing treat quantities: 1, 2, 3, …, 9, and 10 treats. This totals 55 treats per trials for a total of 550 treats. The over- and under- dispensation rates, along with jamming events, are recorded in the following tables. The mean error rate for the six dispensers is calculated, along with the mean error for each trial amount. This procedure was performed for the five dispensers that were built for the Canine Cognition and Human Interaction Laboratory.

Table 1 – Results of the dispenser trials

| Total Treats Dispensed | Correct Number Dispensed | Over-Dispensed | Under-Dispensed
Dispenser One | 550 | 542 | 8 | 1
Dispenser Two | 550 | 543 | 7 | 0
Dispenser Three | 550 | 549 | 1 | 0
Dispenser Four | 550 | 548 | 2 | 0
Dispenser Five | 550 | 549 | 1 | 0

Table 2 – Calculated accuracy and error rates of the dispensers

| Accuracy | Error
Dispenser One | 92% | 8%
Dispenser Two | 93% | 7%
Dispenser Three | 98% | 2%
Dispenser Four | 99% | 1%
Dispenser Five | 98% | 2%

Table 3 – Average accuracy and error across the five dispensers

Mean Accuracy | Mean Error
96% | 4%

The trails shows that any dispensing command has a 4% chance of failing. Considering that the number of treats affects the possibility of errors occurring, the accuracy and error across all ten treat quantities tested were calculated.

Table 4 – Cross quantity accuracy and error metrics

| Accuracy | Error
One Treat | 100% | 0%
Two Treats | 100% | 0%
Three Treats | 100% | 0%
Four Treats | 100% | 0%
Five Treats | 100% | 0%
Six Treats | 98% | 2%
Seven Treats | 100% | 0%
Eight Treats | 84% | 16%
Nine Treats | 94% | 6%
Ten Treats | 86% | 14%

The table above shows that dispensing less than eight treats has the highest likelihood of success in all cases. The raw data is available in the GitHub repository.

Bill of Materials

Bill of Materials – Precise Dispenser
Part | Quantity | Cost | Link
1 kg black filament | 1 | $ 22.99 | Filament (https://www.amazon.com/OVERTURE-Filament-Consumables-Dimensional-Accuracy/dp/B07PGY2JP1)
Raspberry Pi 4 | 1 | $ 55.00 | Raspberry Pi (https://www.sparkfun.com/products/15447)
HDMI Panel Mount | 1 | $ 7.95 | HDMI (https://www.digikey.com/en/products/detail/4054/1528-2888-ND/9997693?itemSeq=352933947)
USB C Panel Mount | 1 | $ 7.50 | USB C (https://www.digikey.com/en/products/detail/4261/1528-4261-ND/10287031?itemSeq=352933946)
Barrel Jack Panel Mount | 1 | $ 5.17 | Barrel Jack (https://www.digikey.com/en/products/detail/10-02879/839-1449-ND/8635386?itemSeq=352933944)
HDMI to Micro HDMI | 1 | $ 8.69 | Micro HDMI (https://www.amazon.com/GANA-Adapter-Female-Action-Supported/dp/B07K21HSQX)
Stepper Motor Power Supply | 1 | $ 11.61 | 12V Power (https://www.digikey.com/en/products/detail/tensility-international-corp/16-00143/10324430)
Stepper Motor | 1 | $ 8.99 | Motor (https://www.amazon.com/gp/product/B087BWKJZP/ref=ox_sc_act_title_1?smid=A2TMK1RHV496EY&th=1)
Raspberry Pi Power Supply | 1 | $ 8.00 | Pi Power (https://www.sparkfun.com/products/15448)
Plastic Cover | 1 | $ 9.95 | 8 in Cover (https://www.amazon.com/gp/product/B083HNZWK6/ref=ox_sc_act_title_2?smid=A2PYYAAPQIARBH&psc=1)
IR Break Beam | 1 | $ 1.95 | 3mm IR (https://www.adafruit.com/product/2167)
M3 Screws | 1 | $ 26.99 | M3 Pack (https://www.amazon.com/gp/product/B083SGJ7BD/ref=ppx_yo_dt_b_search_asin_title?ie=UTF8&psc=1)
M3 Hex Wrench | 1 | $ 14.99 | Hex Set (https://www.amazon.com/gp/product/B06XP16Q4W/ref=ppx_yo_dt_b_asin_title_o01_s00?ie=UTF8&th=1)
Cable Ties | 1 | $ 9.69 | Zip Ties and Mounts (https://www.amazon.com/gp/product/B08F77YVYB/ref=ppx_yo_dt_b_asin_title_o00_s00?ie=UTF8&psc=1)
Micro SD Card | 1 | $ 9.49 | SD Card Pack (https://www.amazon.com/Micro-Center-Class-Memory-Adapter/dp/B07K835MNR)
USB C Cable | 1 | $ 6.99 | USB C Cables (https://www.amazon.com/JXMOX-Charger-Charging-Compatible-2018-Grey/dp/B07TVMBZ75)

Bill of Materials – Precise Dispenser Pi HAT
Part | Quantity | Cost | Link
PCB | 3 | $ 28.45 | [Add OSHPark Link]
A4988 Stepper Motor | 1 | $ 4.69 | Motor Driver (https://www.amazon.com/HiLetgo-Stepstick-Stepper-Printer-Compatible/dp/B00LOF1CA2)
2 Pin Screw Terminal | 2 | $ 2.20 | 2x 3.5mm Terminal (https://www.digikey.com/en/products/detail/w%C3%BCrth-elektronik/691214110002S/11477397)
3 Pin Screw Terminal | 1 | $ 1.35 | 3x 3.5mm Terminal (https://www.digikey.com/en/products/detail/w%C3%BCrth-elektronik/691214110003S/11477432)
Capacitor | 1 | $ 0.13 | 10u TH Cap (https://www.digikey.com/en/products/detail/w%C3%BCrth-elektronik/860240572001/5729254)
Resistor | 1 | $ 0.10 | 10k TH Res (https://www.digikey.com/en/products/detail/stackpole-electronics-inc/CF14JT10K0/1741265)
40 Pin Header | 1 | $ 0.95 | Pi Header (https://www.sparkfun.com/products/16581)
Stepper Motor Header | 1 | $ 0.20 | 4 Pin Right Angle (https://www.digikey.com/en/products/detail/harwin-inc/M20-9750446/3727931)
A4988 Female Pins | 2 | $ 1.30 | 2x Female Headers (https://www.digikey.com/en/products/detail/sullins-connector-solutions/PPTC081LFBN-RC/810147)

Document Revision History

Revision, Name, and Date | Revision Description
V0.1, Walker Arce, 7 March 2021 | First draft creation date for the precise dispenser
V0.2, Walker Arce, 3 April 2021 | Added Python driver documentation
V0.3, Walker Arce, 9 April 2021 | Added Python interfacing example and bills of material
V0.4, Walker Arce, 20 September 2021 | Added build, test, and troubleshooting instructions

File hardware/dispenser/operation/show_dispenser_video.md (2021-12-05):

https://user-images.githubusercontent.com/22334349/144327780-db5506b4-9ede-443f-9127-10286eb5efe3.MOV

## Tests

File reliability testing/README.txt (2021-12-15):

ReadMe file
Created on 2021-12-15 by Jeffrey R. Stevens (jeffrey.r.stevens@gmail.com)

**********************************************************
If you use the data, please cite the following:
Arce, W., & Stevens, J. R. (2021). Computer-controlled dog treat dispenser.
**********************************************************

Summary: We tested five treat dispensers 100 times each with 10 tests of increasing dispensing targets from 1 to 10 treats. Each row of the data file gives the expected and actual number of treats dispensed for a single trial.

License:
All materials presented here are released under the Creative Commons Attribution 4.0 International Public License (CC BY 4.0). You are free to:
    Share — copy and redistribute the material in any medium or format
    Adapt — remix, transform, and build upon the material for any purpose, even commercially.
Under the following terms:
    Attribution — You must give appropriate credit, provide a link to the license, and indicate if changes were made. You may do so in any reasonable manner, but not in any way that suggests the licensor endorses you or your use.
    No additional restrictions — You may not apply legal terms or technological measures that legally restrict others from doing anything the license permits.

Data files:
arce_stevens_2021_data.csv
 dispenser - dispenser number (1-5)
 expected - expected number of treats dispensed (1-10)
 actual - actual number of treats dispensed (1-10)

R code:
 arce_stevens_2021_rcode.R - code for running computations

Instructions to reproduce results:
 To reproduce these results, open arce_stevens_2021_rcode.R and ensure that all packages mentioned at the top of the script are installed.  Once all packages are installed, run the script in R using "source("arce_stevens_2021_rcode.R")".

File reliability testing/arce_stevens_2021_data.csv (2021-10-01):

dispenser | expected | actual
1 | 1 | 1
1 | 2 | 2
1 | 3 | 3
1 | 4 | 4
1 | 5 | 5
1 | 6 | 6
1 | 7 | 7
1 | 8 | 8
1 | 9 | 9
1 | 10 | 10
1 | 1 | 1
1 | 2 | 2
1 | 3 | 3
1 | 4 | 4
1 | 5 | 5
1 | 6 | 6
1 | 7 | 7
1 | 8 | 8
1 | 9 | 9
1 | 10 | 10
1 | 1 | 1
1 | 2 | 2
1 | 3 | 3
1 | 4 | 4
1 | 5 | 5
1 | 6 | 5
1 | 7 | 7
1 | 8 | 9
1 | 9 | 9
1 | 10 | 10
1 | 1 | 1
1 | 2 | 2
1 | 3 | 3
1 | 4 | 4
1 | 5 | 5
1 | 6 | 6
1 | 7 | 7
1 | 8 | 8
1 | 9 | 9
1 | 10 | 12
1 | 1 | 1
1 | 2 | 2
1 | 3 | 3
1 | 4 | 4
1 | 5 | 5
1 | 6 | 6
1 | 7 | 7
1 | 8 | 8
1 | 9 | 9
1 | 10 | 11
1 | 1 | 1
1 | 2 | 2
1 | 3 | 3
1 | 4 | 4
1 | 5 | 5
1 | 6 | 6
1 | 7 | 7
1 | 8 | 9
1 | 9 | 9
1 | 10 | 10
1 | 1 | 1
1 | 2 | 2
1 | 3 | 3
1 | 4 | 4
1 | 5 | 5
1 | 6 | 6
1 | 7 | 7
1 | 8 | 8
1 | 9 | 9
1 | 10 | 11
1 | 1 | 1
1 | 2 | 2
1 | 3 | 3
1 | 4 | 4
1 | 5 | 5
1 | 6 | 6
1 | 7 | 7
1 | 8 | 8
1 | 9 | 9
1 | 10 | 10
1 | 1 | 1
1 | 2 | 2
1 | 3 | 3
1 | 4 | 4
1 | 5 | 5
1 | 6 | 6
1 | 7 | 7
1 | 8 | 8
1 | 9 | 10
1 | 10 | 10
1 | 1 | 1
1 | 2 | 2
1 | 3 | 3
1 | 4 | 4
1 | 5 | 5
1 | 6 | 6
1 | 7 | 7
1 | 8 | 8
1 | 9 | 10
1 | 10 | 10
2 | 1 | 1
2 | 2 | 2
2 | 3 | 3
2 | 4 | 4
2 | 5 | 5
2 | 6 | 6
2 | 7 | 7
2 | 8 | 9
2 | 9 | 9
2 | 10 | 10
2 | 1 | 1
2 | 2 | 2
2 | 3 | 3
2 | 4 | 4
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

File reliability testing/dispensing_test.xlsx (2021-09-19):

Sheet: Prototype Dispenser
Full Step Resolution |  |  |  | Half Step Resolution
Chosen | Actual | Error | Error Count | Chosen | Actual | Error | Error Count
1 | 1 | 0 | 2 | 1 | 1 | 0 | 1
2 | 2 | 0 | Tests | 2 | 2 | 0 | Tests
3 | 3 | 0 | 100 | 3 | 3 | 0 | 100
4 | 4 | 0 | Error Rate | 4 | 4 | 0 | Error Rate
5 | 5 | 0 | 2% | 5 | 5 | 0 | 1%
6 | 6 | 0 |  | 6 | 7 | 1
7 | 7 | 0 |  | 7 | 7 | 0
8 | 8 | 0 |  | 8 | 8 | 0
9 | 9 | 0 |  | 9 | 9 | 0
10 | 10 | 0 |  | 10 | 10 | 0
1 | 1 | 0 |  | 1 |  | -1
2 | 2 | 0 |  | 2 |  | -2
3 | 3 | 0 |  | 3 |  | -3
4 | 4 | 0 |  | 4 |  | -4
5 | 5 | 0 |  | 5 |  | -5
6 | 6 | 0 |  | 6 |  | -6
7 | 7 | 0 |  | 7 |  | -7
8 | 9 | 1 |  | 8 |  | -8
9 | 9 | 0 |  | 9 |  | -9
10 | 10 | 0 |  | 10 |  | -10
1 | 1 | 0 |  | 1 |  | -1
2 | 2 | 0 |  | 2 |  | -2
3 | 3 | 0 |  | 3 |  | -3
4 | 4 | 0 |  | 4 |  | -4
5 | 5 | 0 |  | 5 |  | -5
6 | 7 | 1 |  | 6 |  | -6
7 | 7 | 0 |  | 7 |  | -7
8 | 8 | 0 |  | 8 |  | -8
9 | 9 | 0 |  | 9 |  | -9
10 | 10 | 0 |  | 10 |  | -10
1 | 1 | 0 |  | 1 |  | -1
2 | 2 | 0 |  | 2 |  | -2
3 | 3 | 0 |  | 3 |  | -3
4 | 4 | 0 |  | 4 |  | -4
5 | 5 | 0 |  | 5 |  | -5
6 | 6 | 0 |  | 6 |  | -6
7 | 7 | 0 |  | 7 |  | -7
8 | 8 | 0 |  | 8 |  | -8
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

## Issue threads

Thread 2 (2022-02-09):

### ISSUE TITLE
Improved design for you.

### ISSUE THREAD

**Issue by GravisZro** [unl-cchil/canine_precise_dispenser#2]
There is actually a _much_ simpler design that would maximize accuracy beyond the current design.  The primary mechanism you should be using is called a [vibratory bowl feeder](https://en.wikipedia.org/wiki/Bowl_feeder) which is deceptively simple but can be used to individually dispense a large number of dog treats of any weight, shape, or size.  [You can 3d print one](https://bytechlab.com/2018/07/smd-parts-bowl-feeder-prototype/) though it's simple enough that the bowl could be cold stamped in your metal of choice.

The downside is that it is slow, so you want a preparatory area that the treat will fall onto.  There are different needs for different experiments, so there should be multiple preparatory area designs.

If you need the ability to rapidly dispense an unknown number of treats until moments before they are dispensed then the preparatory area could be a small conveyor belt.  At the end of the conveyor belt the treats would fall to be dispensed.  How to sense the treat is on the conveyor belt is an exercise left to the reader. ;)

If you know the number of treats to dispense ahead of time then you can just have them fall into a preparatory area with a load cell to count the number of treats.  The preparatory area could actuate like a trap door to dispense the treats.  A simple servo could accomplish this.

**Comment by wsarce** [comment]
Thanks for the feedback!  I agree that there may be better ways to achieve a precise dispenser, I just didn't find any complete open source designs for one intended for the type of research done by Jeff, so I designed one that included everything needed to generate stimulus, take input from a touchscreen, and dispense a precise number of treats.  The diagram for this approach can be found [here](https://github.com/unl-cchil/canine_treat_dispenser/blob/master/documentation/figures/figure2.png), which is a similar setup to what we used for this dispenser, but we did without the embedded system and leveraged the Raspberry Pi.  This was a direct development from our [Treat & Train retrofit dispenser](https://github.com/unl-cchil/canine_treat_dispenser), so we borrowed a lot of ideas from that development.

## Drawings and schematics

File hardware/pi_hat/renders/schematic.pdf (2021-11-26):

2B | 14 VDD | 10 VMOT | 16 GND | 9*2

A

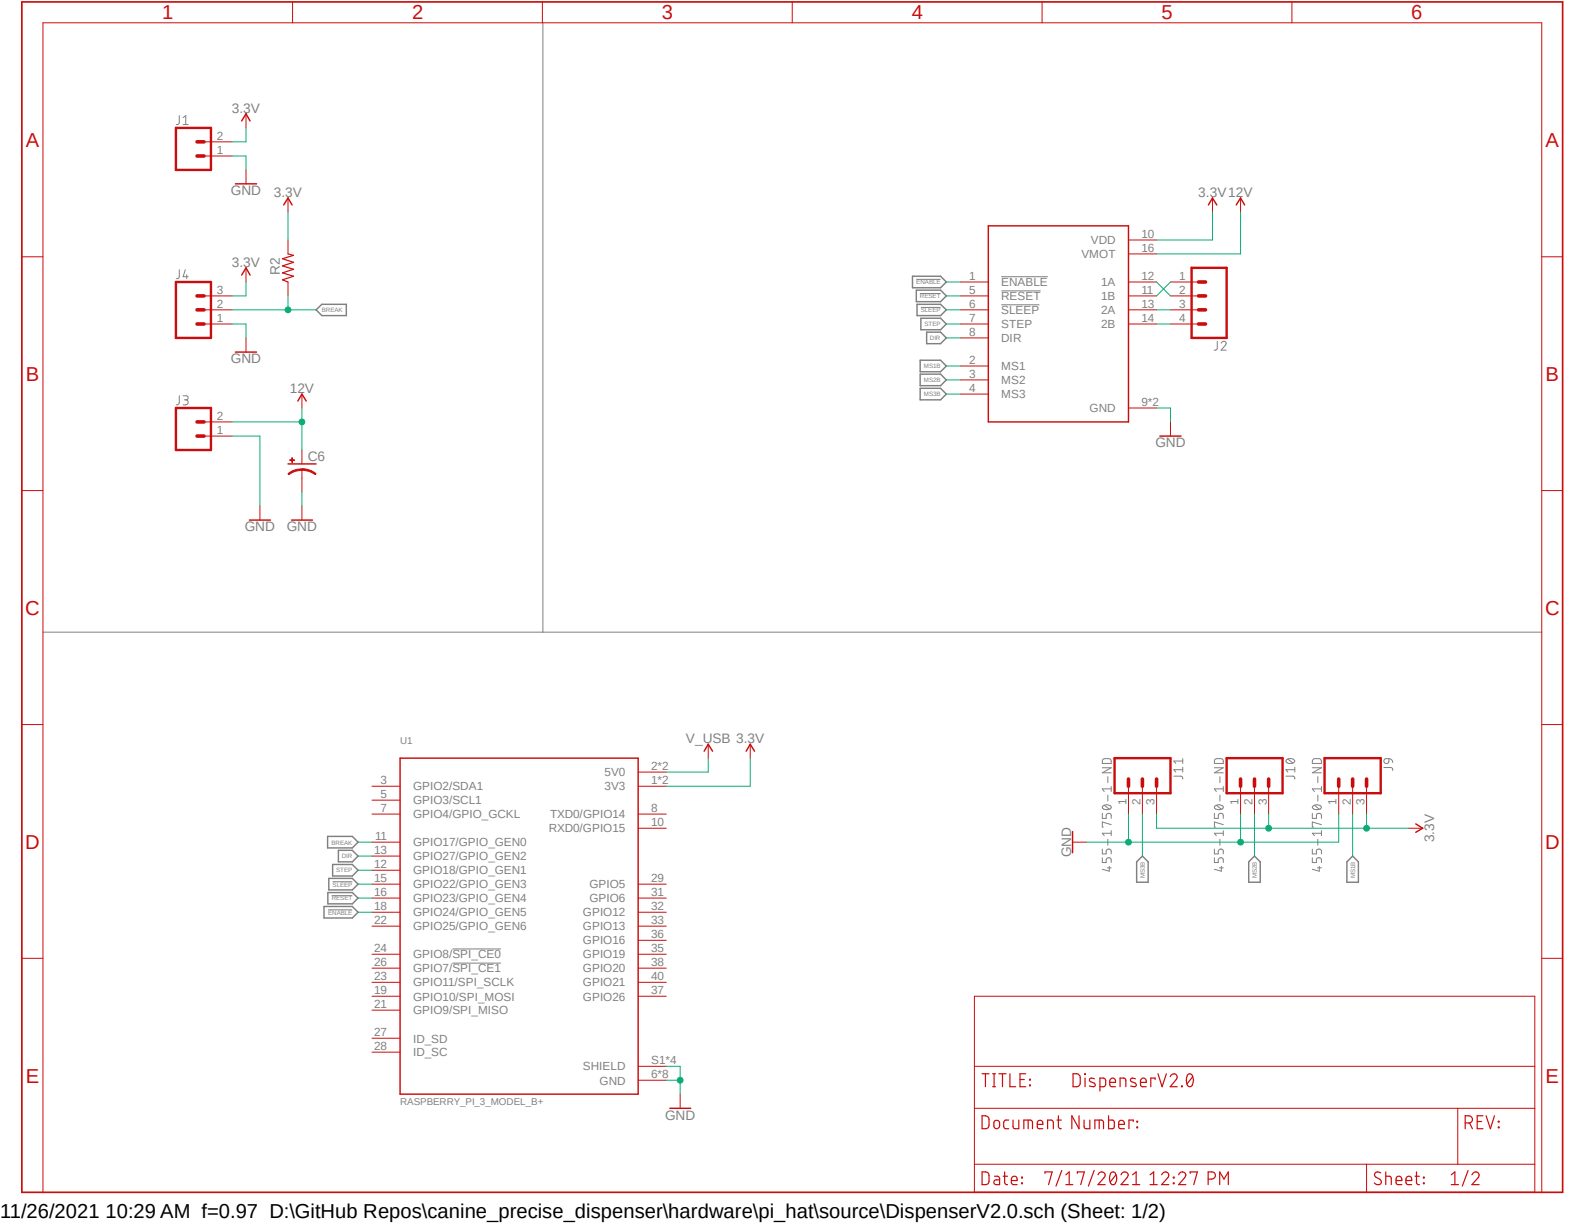
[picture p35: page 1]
V_USB; GND; GND GND; 3.3V GND; GND 3.3V; RASPBERRY_PI_3_MODEL_B+; ENABLE 1; 12 RESET 5; SLEEP 6; STEP 7; DIR 8; 1*2 GPIO2/SDA1 3; GPIO3/SCL1 5; GPIO4/GPIO_GCKL 7; TXD0/GPIO14; 8 GND; RXD0/GPIO15; 10 GPIO17/GPIO_GEN0 11; GPIO18/GPIO_GEN1 12; GPIO27/GPIO_GEN2 13; GPIO22/GPIO_GEN3 15; GPIO23/GPIO_GEN4 16; GPIO24/GPIO_GEN5 18; GPIO10/SPI_MOSI 19; GPIO9/SPI_MISO 21; GPIO25/GPIO_GEN6 22; GPIO11/SPI_SCLK 23; GPIO8/SPI_CE0 24; GPIO7/SPI_CE1 26; GPIO5; 29 GPIO6; 31 GPIO12; 32 GPIO13; 33 GPIO19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

11/26/2021 10:29 AM f=0.97 D:\GitHub Repos\canine_precise_dispenser\hardware\pi_hat\source\DispenserV2.0.sch (Sheet: 1/2)

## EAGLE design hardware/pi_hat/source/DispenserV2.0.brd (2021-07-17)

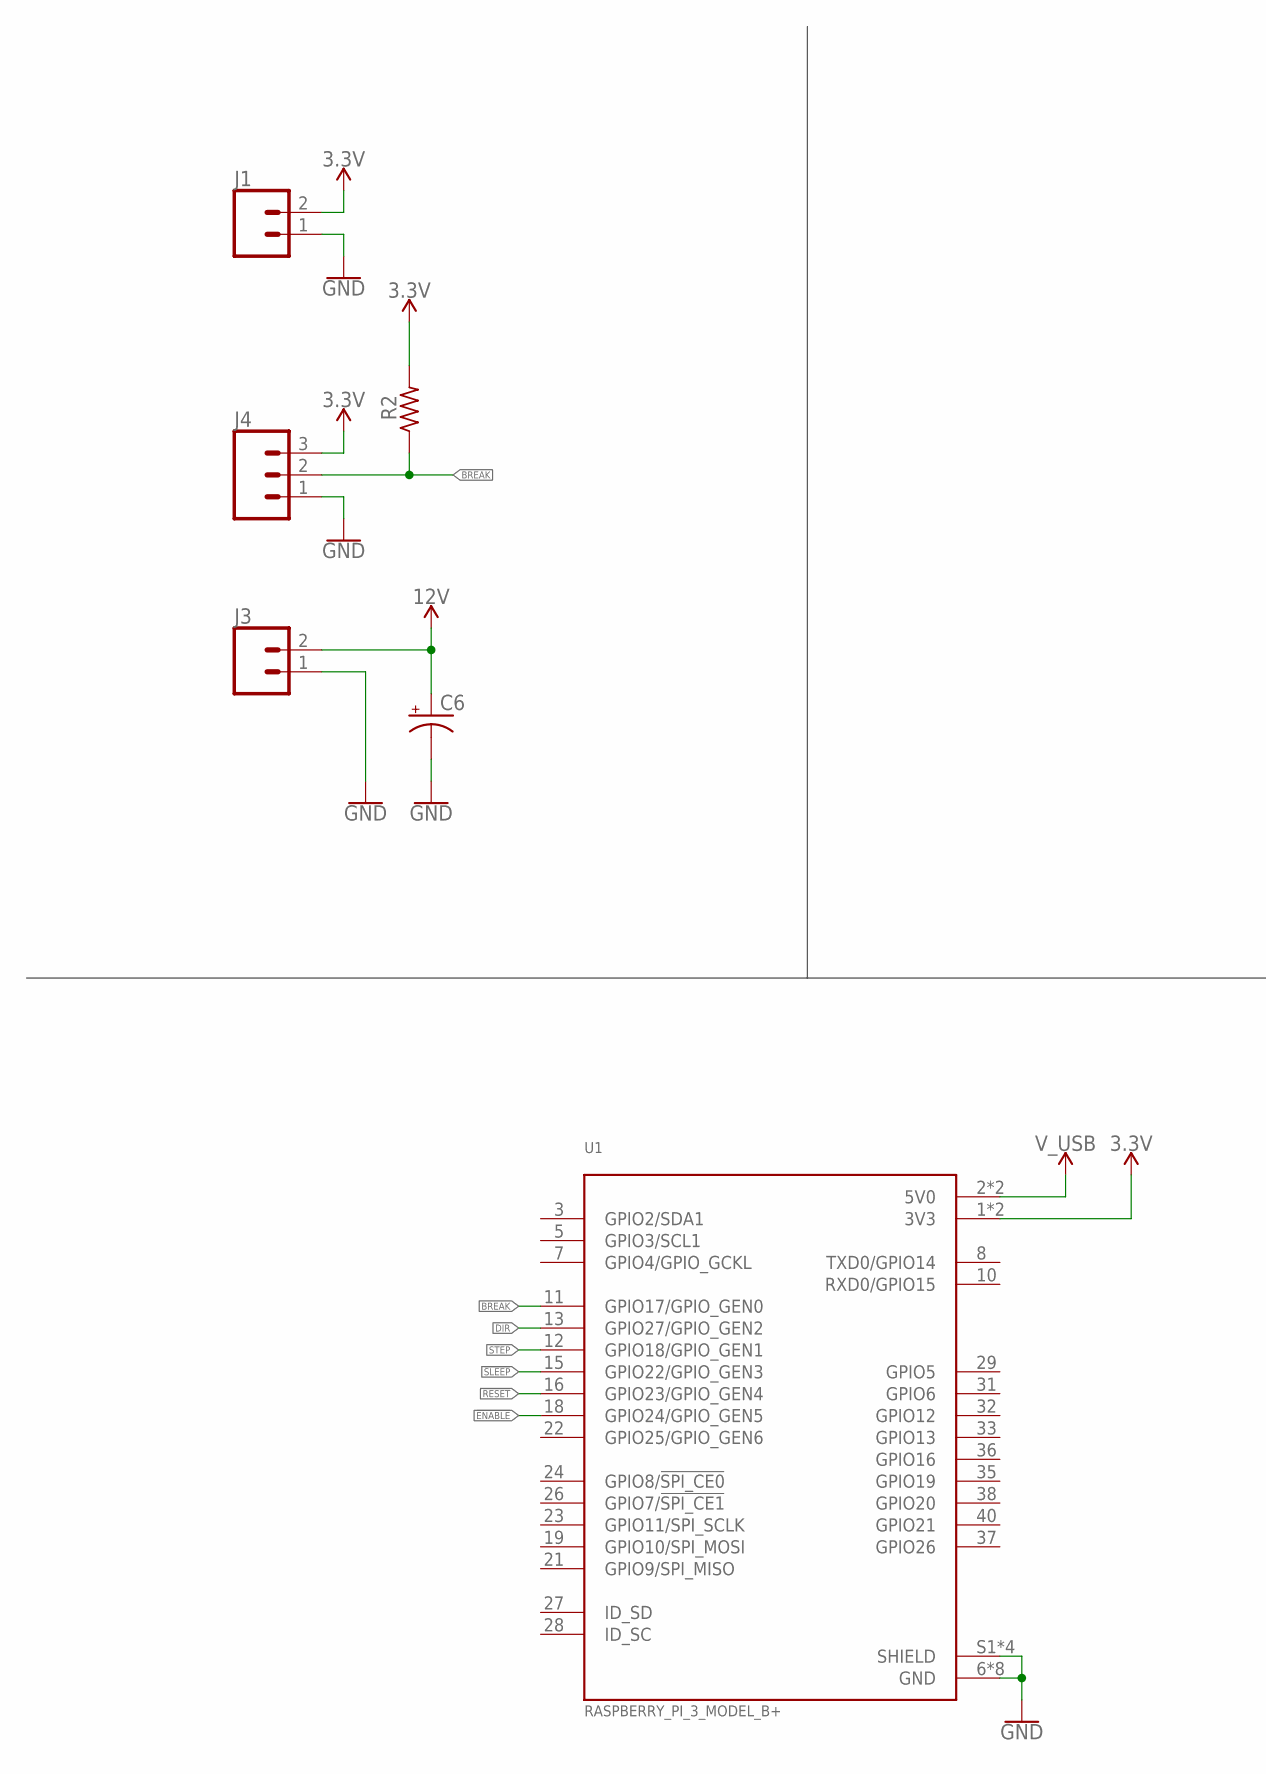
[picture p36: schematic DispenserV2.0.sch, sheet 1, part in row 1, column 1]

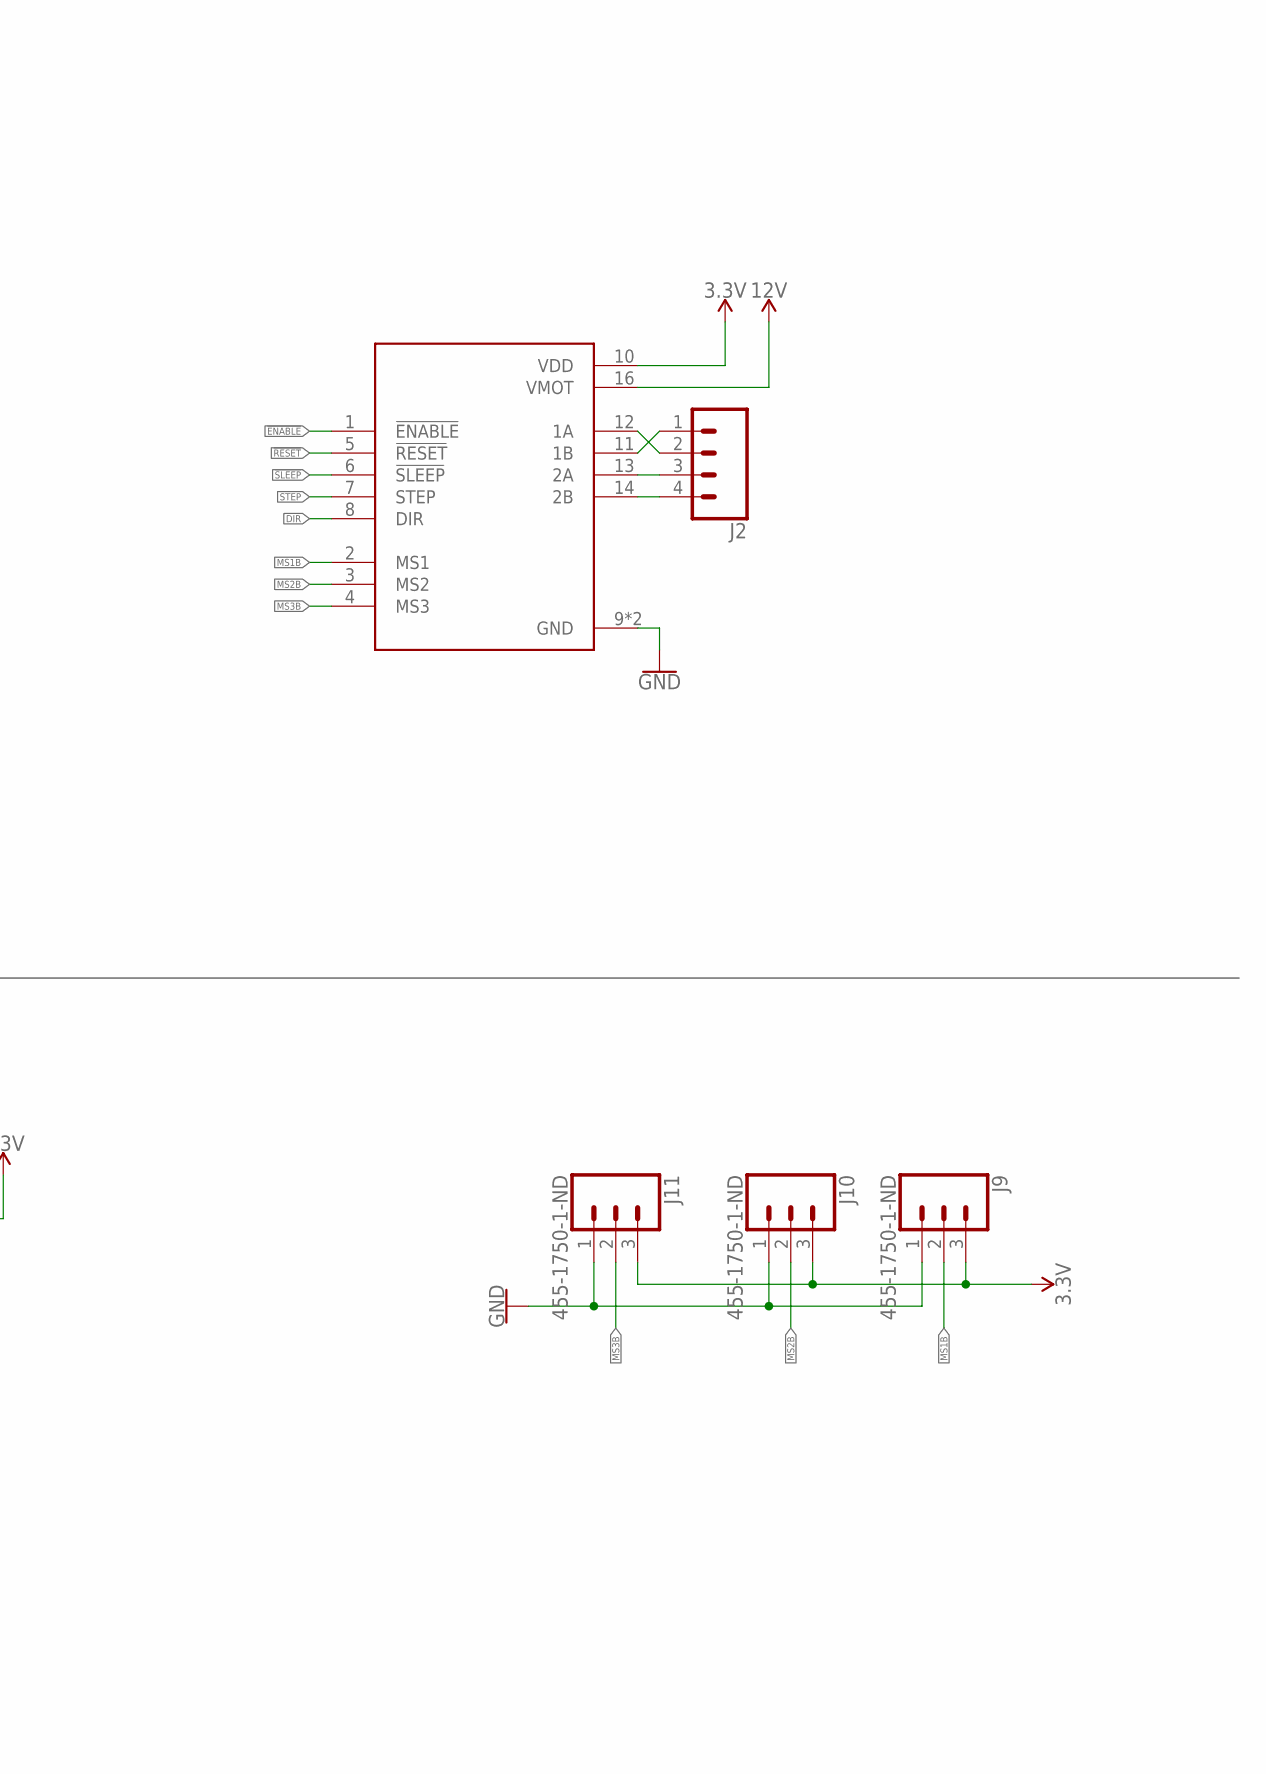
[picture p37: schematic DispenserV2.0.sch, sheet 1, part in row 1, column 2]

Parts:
C6: CPOL-USE2-5; E2-5
J1, J3: CONN_023.5MM; SCREWTERMINAL-3.5MM-2
J2: CONN_04; 1X04
J4: CONN_03SCREW; SCREWTERMINAL-3.5MM-3
J9, J10, J11: 455-1750-1-ND; 1X03
R2: R-US_0207/10; 0207/10
U1: RASPBERRY_PI_3_MODEL_B+; MODULE_RASPBERRY_PI_3_MODEL_B+
U2: A4988; MODULE_A4988_STEPPER_MOTOR_DRIVER_CARRIER

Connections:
3.3V: J1.2, J4.3, J9.3, J10.3, J11.3, R2.2, U1.1 (3V3), U1.17 (3V3), U2.10 (VDD)
12V: C6.+, J3.2, U2.16 (VMOT)
!ENABLE: U1.18 (GPIO24/GPIO_GEN5), U2.1 (!ENABLE)
!RESET: U1.16 (GPIO23/GPIO_GEN4), U2.5 (!RESET)
!SLEEP: U1.15 (GPIO22/GPIO_GEN3), U2.6 (!SLEEP)
BREAK: J4.2, R2.1, U1.11 (GPIO17/GPIO_GEN0)
DIR: U1.13 (GPIO27/GPIO_GEN2), U2.8 (DIR)
GND: C6.-, J1.1, J3.1, J4.1, J9.1, J10.1, J11.1, U1.6 (GND), U1.9 (GND), U1.14 (GND), U1.20 (GND), U1.25 (GND), U1.30 (GND), U1.34 (GND), U1.39 (GND), U1.S1 (SHIELD), U1.S2 (SHIELD), U1.S3 (SHIELD), U1.S4 (SHIELD), U2.9 (GND), U2.15 (GND)
MS1B: J9.2, U2.2 (MS1)
MS2B: J10.2, U2.3 (MS2)
MS3B: J11.2, U2.4 (MS3)
unnamed: J2.1, U2.11 (1B)
unnamed: J2.3, U2.13 (2A)
unnamed: J2.4, U2.14 (2B)
unnamed: J2.2, U2.12 (1A)
STEP: U1.12 (GPIO18/GPIO_GEN1), U2.7 (STEP)
V_USB: U1.2 (5V0), U1.4 (5V0)

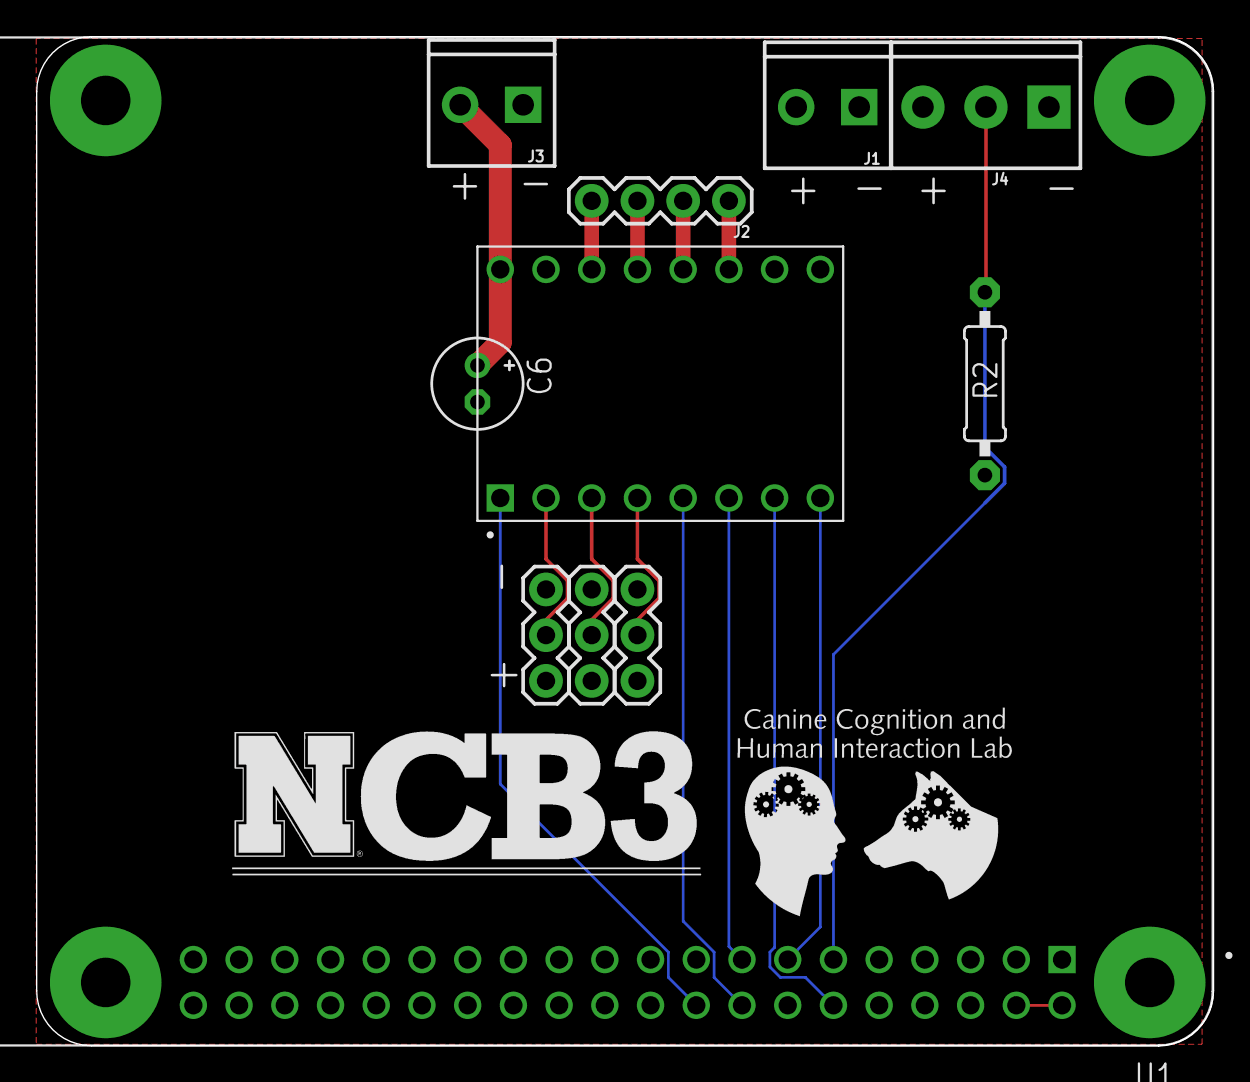
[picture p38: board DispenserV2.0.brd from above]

Board: 2 copper layers, 65.4 x 56.1 mm, 11 parts (0 on the bottom side), 17 nets.

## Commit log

2021-02-08 Bringing repo up to date
    - Added source dispenser 3D model
    - Copied firmware and raspberry pi driver from other dispenser project over
    - Added gcode and stls
    [Dispenser v18.f3d, DispenserV2.0.brd, DispenserV2.0.sch, dispenser_body.stl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]
2021-02-10 Update source model with most recent version
    [Dispenser v22.f3d, dispenser_pi_mount.stl]
2021-02-17 Printing test cover for fitting
2021-03-07 Working on first prototype
    - Dispenser wheel can be controlled using Raspberry Pi
    - Started user guide
    - Removed custom board for the time being along with firmware
    [DispenserV2.0.brd, DispenserV2.0.sch]
2021-03-08 Printing out a test interface to test new fit for connectors
    [dispenser_interface.stl]
2021-03-08 Made changes to dispenser based on testing and fitment
    - Fixed sizing of connector mounting holes
    - Added an inch of height to the dispenser
    - Changed the dispenser hole to be steeper
    - Raised the height of the cover mount
    [Dispenser v30.f3d]
2021-03-10 Added datasheets and updated STL files
    - Fixing the sizing of the panel mount components
    - Added datasheets for panel mount components
    - Updated STLs from testing
    [Dispenser v31.f3d, dispenser_body.stl, dispenser_pellet_exhaust.stl, dispenser_wheel.stl]
2021-03-10 Slicing for a test print of the pellet exhaust
2021-03-11 Resliced and printed the pellet exhaust with IR break beam
    [dispenser_pellet_exhaust.stl]
2021-03-14 Completed first draft of artwork to control the stepper motor and IR break beam
    [DispenserV2.0.brd, DispenserV2.0.sch]
2021-03-26 Updating Pi Hat with changes for break sensor
    [DispenserV2.0.brd, DispenserV2.0.sch]
2021-04-03 Started Python driver for dispenser, tested working on Raspberry Pi
2021-04-03 Updated board to include connectors for break sensors
    [DispenserV2.0.brd, DispenserV2.0.sch]
2021-04-04 Create Dispenser v35.f3d
    Exported current version of dispenser
    [Dispenser v35.f3d]
2021-04-05 Reprinting a test connector interface to finalize fitment
    [dispenser_interface.stl]
2021-04-06 Updated the pellet exhaust with mounting hole for break sensor. Printing the exhaust to test fitment.
    Yesterday's printed backplane interface fits perfectly.
    [Dispenser v39.f3d, dispenser_pellet_exhaust.stl]
2021-04-07 Fixing M3 mounting holes for break sensors, test printing
    [dispenser_pellet_exhaust.stl]
2021-04-08 Mounting points on exhaust work, slicing the body for a full print
    [dispenser_body.stl]
2021-04-08 Slicing dispenser wheel for printing
    [dispenser_wheel.stl]
2021-04-08 Starting on boms
    [pi_hat_bom.xlsx, precise_dispenser_bom.xlsx]
2021-04-09 Completed boms
    [pi_hat_bom.xlsx, precise_dispenser_bom.xlsx]
2021-04-09 Updated boms for Word compatibility, updating user guide
    [pi_hat_bom.xlsx, precise_dispenser_bom.xlsx]
2021-04-11 Working on new version of dispenser with bottom plate and feet
    [Dispenser v55.f3d, dispenser_body.stl, dispenser_bottom.stl, dispenser_cover.stl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]
2021-04-12 Added stepper motor datasheet and working wheel changes
    [dispenser_wheel.stl]
2021-04-16 Performed reliability testing and logged it to spreadsheet, added test script
    [dispensing_test.xlsx]
2021-04-16 Added v67 source, added power DPDT switch
2021-04-16 Update dispenser_walls.stl
    Exported v67 walls
    [dispenser_walls.stl]
2021-04-17 Sliced the last of the dispenser files
    [pi_hat_bom.xlsx, precise_dispenser_bom.xlsx]
2021-04-17 Update SV01_dispenser_bottom.gcode
    Removed skirt from print
2021-04-23 Finalized BOMs
    [dispensing_test.xlsx, pi_hat_bom.xlsx, precise_dispenser_bom.xlsx]
2021-04-23 Fixing clearance issues on 3D printer and fitment between pieces
    [dispenser_bottom.stl]
2021-04-24 Exported v72 source, working on new cover design to affix acrylic plate without glue
    [dispenser_cover.stl]
2021-04-24 Updated bom and resliced the cover and rpi mount
    [precise_dispenser_bom.xlsx]
2021-04-27 Finished export and slicing of final parts
    [dispenser_bottom.stl, dispenser_cover.stl, dispenser_top.stl]
2021-05-02 Updated STLs, exported final version of dispenser
    [dispenser_bottom.stl, dispenser_cover.stl, dispenser_top.stl, dispenser_wheel.stl]
2021-07-17 Updated Pi HAT to fix the Pi header pinout
    [DispenserV2.0.brd, DispenserV2.0.sch]
2021-09-14 Created v84 render, performed some testing for fine tuning
    [dispensing_test.xlsx]
2021-09-18 Completed testing and updated the software
    [dispenser_wheel_2.stl, dispensing_test.xlsx]
2021-09-19 Created Pi HAT renders and created tables from testing
    [DispenserV2.0.step, dispensing_test.xlsx]
2021-10-01 Add data and analysis script for dispensing accuracy
    [arce_stevens_2021_data.csv]
2021-11-26 Exported STEP files and PDF of schematic
    [dispenser_bottom.step, dispenser_cover.step, dispenser_top.step, dispenser_walls.step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]
2021-11-26 Adding details and new figures for paper
    [final_bom.xlsx]

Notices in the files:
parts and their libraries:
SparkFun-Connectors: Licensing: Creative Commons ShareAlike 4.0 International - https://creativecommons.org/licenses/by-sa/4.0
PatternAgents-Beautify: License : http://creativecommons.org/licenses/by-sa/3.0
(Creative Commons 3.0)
